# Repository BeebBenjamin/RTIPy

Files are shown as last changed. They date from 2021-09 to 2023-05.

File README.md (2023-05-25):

## Introduction

RTIPy is a Python and Arduino project designed to power a low complexity, affordable, and portable micro Reflectance
Transformation Imaging (RTI) dome for use in fieldwork.  The RTI dome was commissioned by Dr Abigail Desmond and 
designed and built by Mr Richard Benjamin Allen at Palaeopi Ltd and funded by the Ashmolean Museum, Oxford.

You can see the dome set up as it is intended below in two reference pictures.

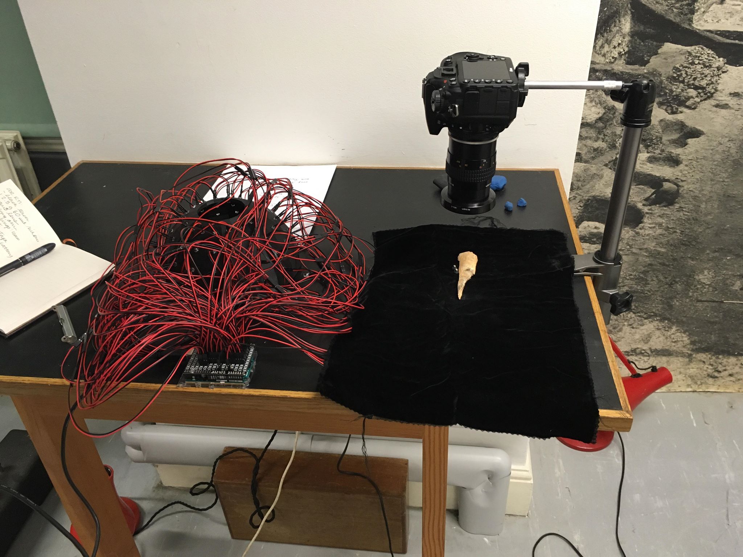
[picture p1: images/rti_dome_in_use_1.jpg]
RTI dome in use 1


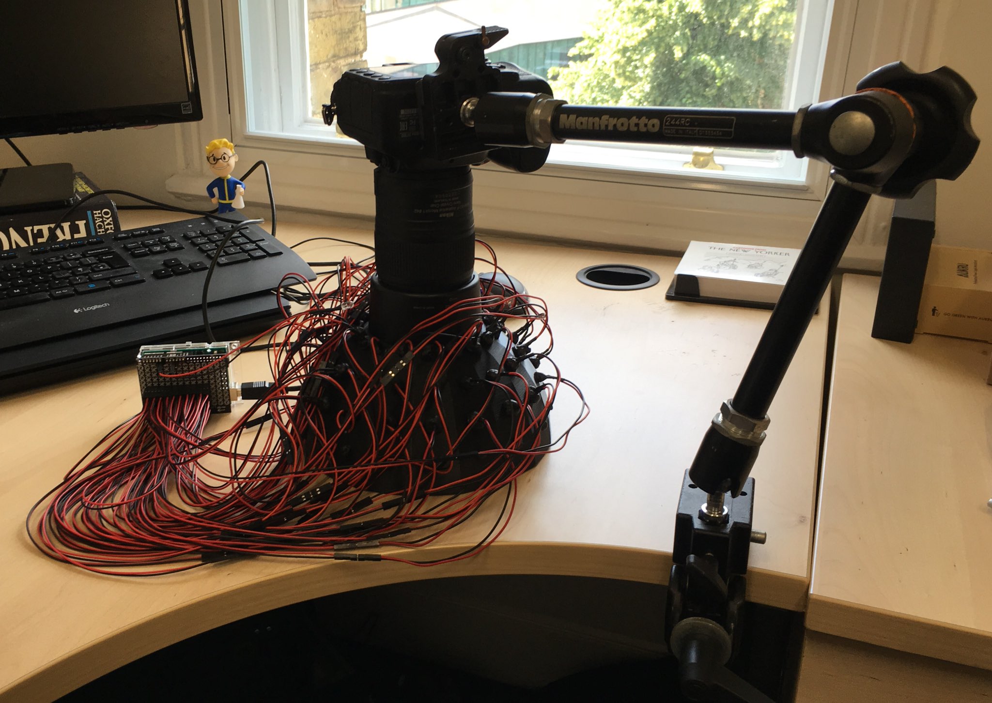
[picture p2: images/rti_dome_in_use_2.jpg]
RTI dome in use 2


## Installation

The project depends on an external Arduino library to drive the Lolshield. Download and install the LoLshield library 
into your Arduino IDE, the project can be found here: https://github.com/jprodgers/LoLshield

Use the Arduino IDE to upload the code from the `arduino/rti_py` directory to the Ardunio Uno in the usual way.

To install the Python script needed to communicate with the Arduino board first install `Python 3.8` and `pipenv` as
per your computer's OS.

**N.B.** Only Linux or MacOS are currently supported by this project.

Then open up a terminal, navigate to the local GitHub repository, and install the required Python packages as follows:

```bash
pipenv install
```

## Changing the Setup File
The project includes a configurable `setup.yml` file, here one can change the various system variables that the
project uses for photography timings e.g. delays required for different exposures; the number of LEDs in use and the
'bounds' of the LEDs e.g. the number and address of the columns and rows used in your setup.  The file itself contains
additional helpful comments that can tell you what each setting does.

## Bill Of Materials
* 1 x Pre-wired 5mm Infra-red 5v LED
* 1 x LoLshield
* Several strips of 2.54 mm un-shrouded pin headers cut into pairs (total of 72 pins in pairs of 2 e.g. 31 pairs)
* 1 x Arduino Uno + USB cable
* 1 x 3D printed dome
* 72 x Dual pin jumper wire with "Dupont" connectors, you can buy them [here](https://shop.pimoroni.com/products/dual-pin-jumper-wire)
* 72 x Pre-wired 5mm clear 5v LED with "Dupont" connectors

## Build Instructions
1. Build the Lolshield (assemble as per it's instructions).  However, if the board comes with its own LEDs don't 
solder them to the board, because we are going to attach our own headers. 

2. Cut up the 2.54mm pin headers into pairs and solder these in rows and columns into the area marked in the following image, note that each pair sits
inside the white circle.  You may need to trim the extra plastic off the sides to get them to fit nicely together, a small file will do the job well:

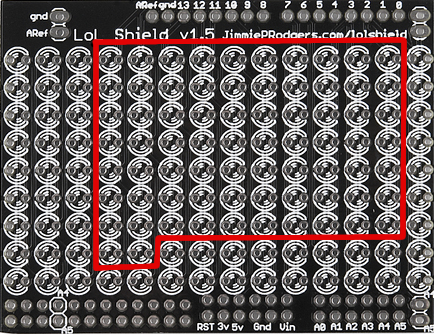
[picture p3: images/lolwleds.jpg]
white led pins


2. Solder a header pin to analogue pin A0 and to a ground pin for the IR LED as follows:

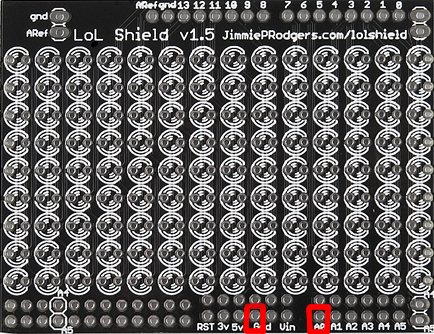
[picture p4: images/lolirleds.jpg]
ir led pins


3. Attach the Lolshield to the Arduino Uno by pushing it into place like many of the available Arduino shields.

4. Connect the jumper leads to the pre-wired white light LEDs and link them up to the headers on the Lolshield, making
sure that the polarity is correct.  Next connect up the pre-wired IR LED to analogue pins A0 and ground.

5. Insert the white light LEDs into the holes of the 3D printed dome, use blue-tack or something similar to secure them
if the fittings are loose.

6. Plug the Arduino into a USB port on your computer to power the device; you will need to use serial over USB to
also send instructions to the device.

7. Set up your camera as you usually would for RTI and position it over the hole in the top of the dome, use a
cloth to cover the dome if you wish.  [See Basic Usage](#basic-usage) for how to pilot the dome using the computer terminal. 

## 3D Printed Files
There is a 3D printable dome in the project files, this can be printed using many types of 3D printer or material. 
For best results the model should be re-sized/calibrated so that the LED holes are not too loose upon printing.

## RTI Spheres
We found that 5mm steel balls extracted from roller bearings make excellent RTI spheres for macro photography.  These
can be superglued to [Lego studs with holes](https://www.brickowl.com/catalog/lego-white-plate-1-x-1-round-with-open-stud-28626-85861)
and their height can easily be adjusted by adding Lego plates to the bottom of the stud.

## Camera Compatibility
The Arduino code is designed to work with Nikon DSLRs with IR trigger capability.  These have unfortunately been
phased out of the most recent models.  If you want to make it work with different camera makes (or more modern Nikons), 
you will need to change the IR pulse code accordingly or find another method of triggering the camera.

## Basic Usage
### Turning on a light for adjusting camera focus and exposure
Open a terminal and change directory to the place where you downloaded the RTIPy repository.  Activate the pipenv 
environment previously installed during [installation](#Installation) by typing in the following command into the 
terminal and press enter:

```bash
pipenv shell
```
Next type the following command into the terminal and press enter:

```bash
python rti_py.py -l
```

A single LED should light up inside which will allow you to adjust the camera exposure and the timings in the `setup.yml`
file accordingly.

### Adjusting the angle of individual LEDs
If you notice that a particular LED needs adjusting (probably during post processing) it is possible to follow the LED
back to the board, find its column and row address and instruct the board to light it; this should allow you to adjust 
the angle with the blue tack if it is a particularly loose fit.  To do so type the something like following command into 
the terminal and press enter, where the numbers following mean column, row, and duration in seconds:

```bash
python rti_py.py -c 3,0,20
```

A single LED should light up inside which will allow you to adjust its angle shining onto the target object or use it
to calibrate the camera as per the `-l` command.

### Triggering Capture
To trigger the capture sequence, activate the IR release mode on your Nikon camera in the menu and make sure it can "see"
the IR trigger LED.  Next type the following command into the terminal and press enter:

```bash
python rti_py.py -s
```

Remember that if you require different delays for different camera exposures, these can be adjusted using the `setup.yml`
config file.

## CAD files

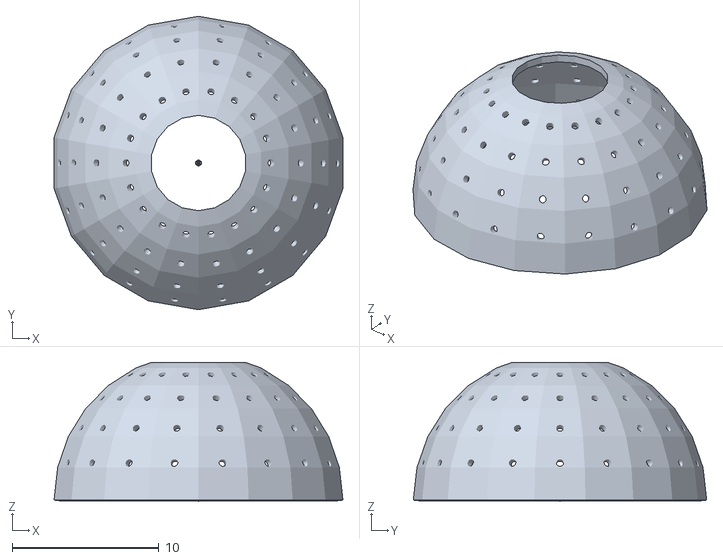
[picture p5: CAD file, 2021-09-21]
3d files/rti_dome.stl
19.7 x 20.0 x 9.49
